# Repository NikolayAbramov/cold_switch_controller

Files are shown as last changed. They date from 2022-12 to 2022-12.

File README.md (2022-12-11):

# Cold switch controller
This is the specialized polarized relay controller intended to drive an RF switches, installed inside a cryostat. It's mainly
affordable for switches similar to famous Radial products: https://www.radiall.com/products/rf-microwave-switches.html. Such switches are commonly used in experiments with superconducting RF devices, and, particularly, with quantum circuits. 

The first problem with such switches at the liquid He temperature 4K and below is that the resistance of their coils drops by ~100 times compared to room temperature values and it's no longer possible to drive them with a nominal voltage. The second is that the heat dissipation during switching must be controlled to ensure normal cryostat operation. I't especially important in case of dilution refrigerators, commonly used for experiments with quantum devices. 

To overcome the above mentioned problems the controller uses an adjustable pulsed current source instead of a voltage source to drive the coils. Both the current and pulse duration can be adjusted to achieve a reliable switching and a minimal power dissipation. Due to it's flexibility, the controller can be used to control RF switches also at room temperature which makes it a useful tool to have in you lab for test and experiment automation.

It has a minimalistic formfactor of a 3U Eurorack module with absolutely no cotrols - everything is done using a web interface or an SCPI commands.

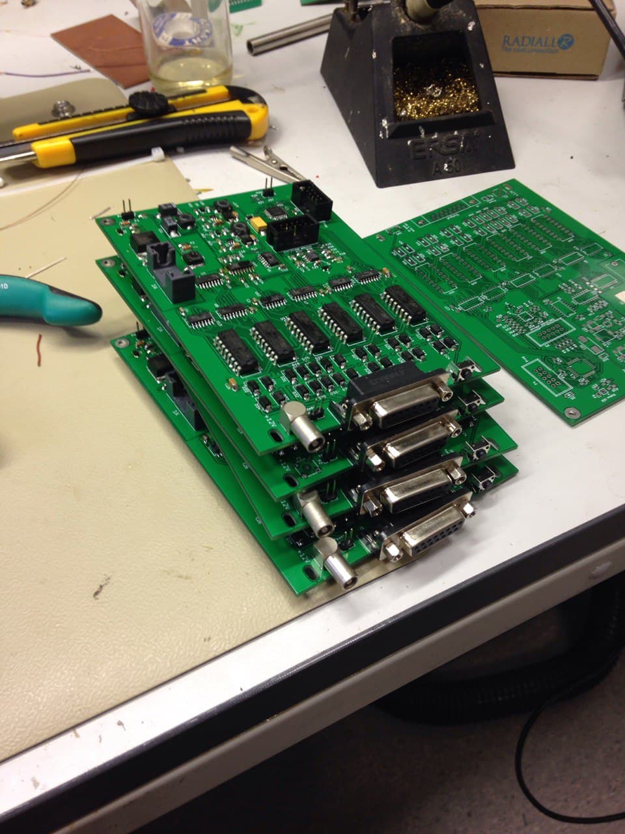
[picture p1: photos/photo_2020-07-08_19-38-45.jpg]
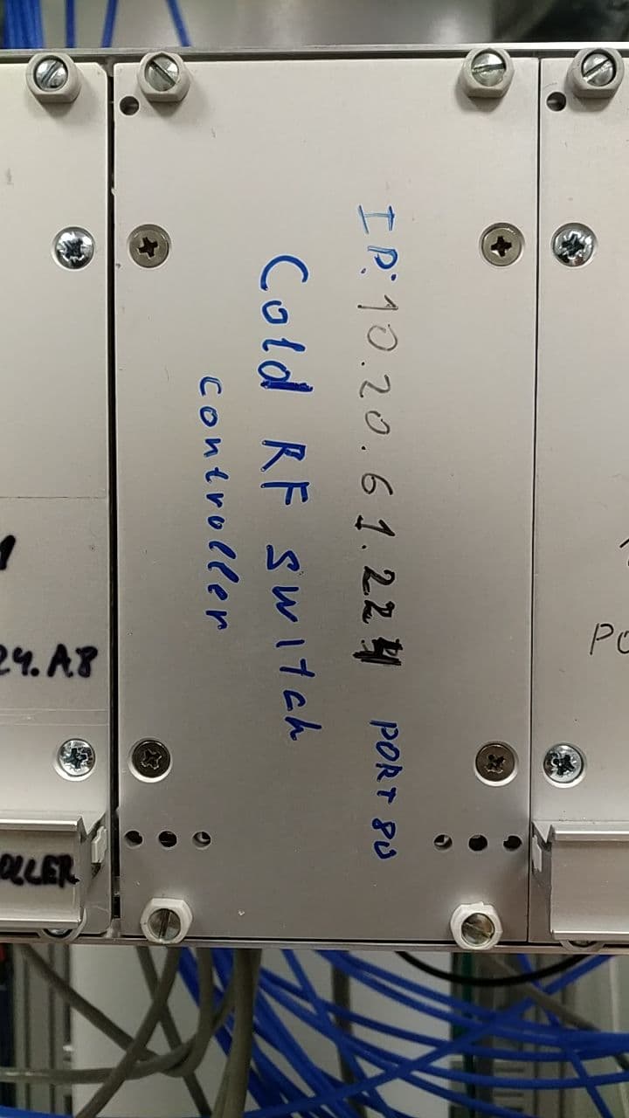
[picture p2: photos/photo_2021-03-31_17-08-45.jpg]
 

# Specs

 - Power: 12V, fully protected against overvoltage up to 30V and reversed polarity
 - Interface: Ethernet with web interface and SCPI commands
 - Output: 2 channels for polarized SPnT switches with number of positions n up to 6
 - Drive current: 10-600 mA
 - Drive pulse width: 1 - 700 ms
 - Switch coil voltage: 12 V for room temperature operation, any for cryogenic applications

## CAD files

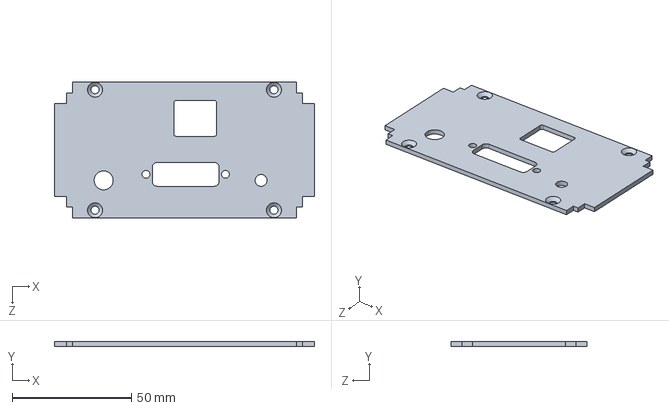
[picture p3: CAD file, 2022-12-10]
EuroBox_rear_panel/switch_controller_rear.SLDPRT
109.0 x 2.00 x 57.0 mm

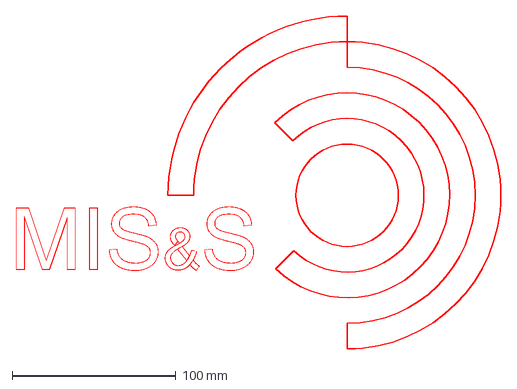
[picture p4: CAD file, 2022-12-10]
kicad/Logo_MISiS.dxf
295.7 x 203.1 mm

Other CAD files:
EuroBox_rear_panel/switch_controller_rear.SLDDRW

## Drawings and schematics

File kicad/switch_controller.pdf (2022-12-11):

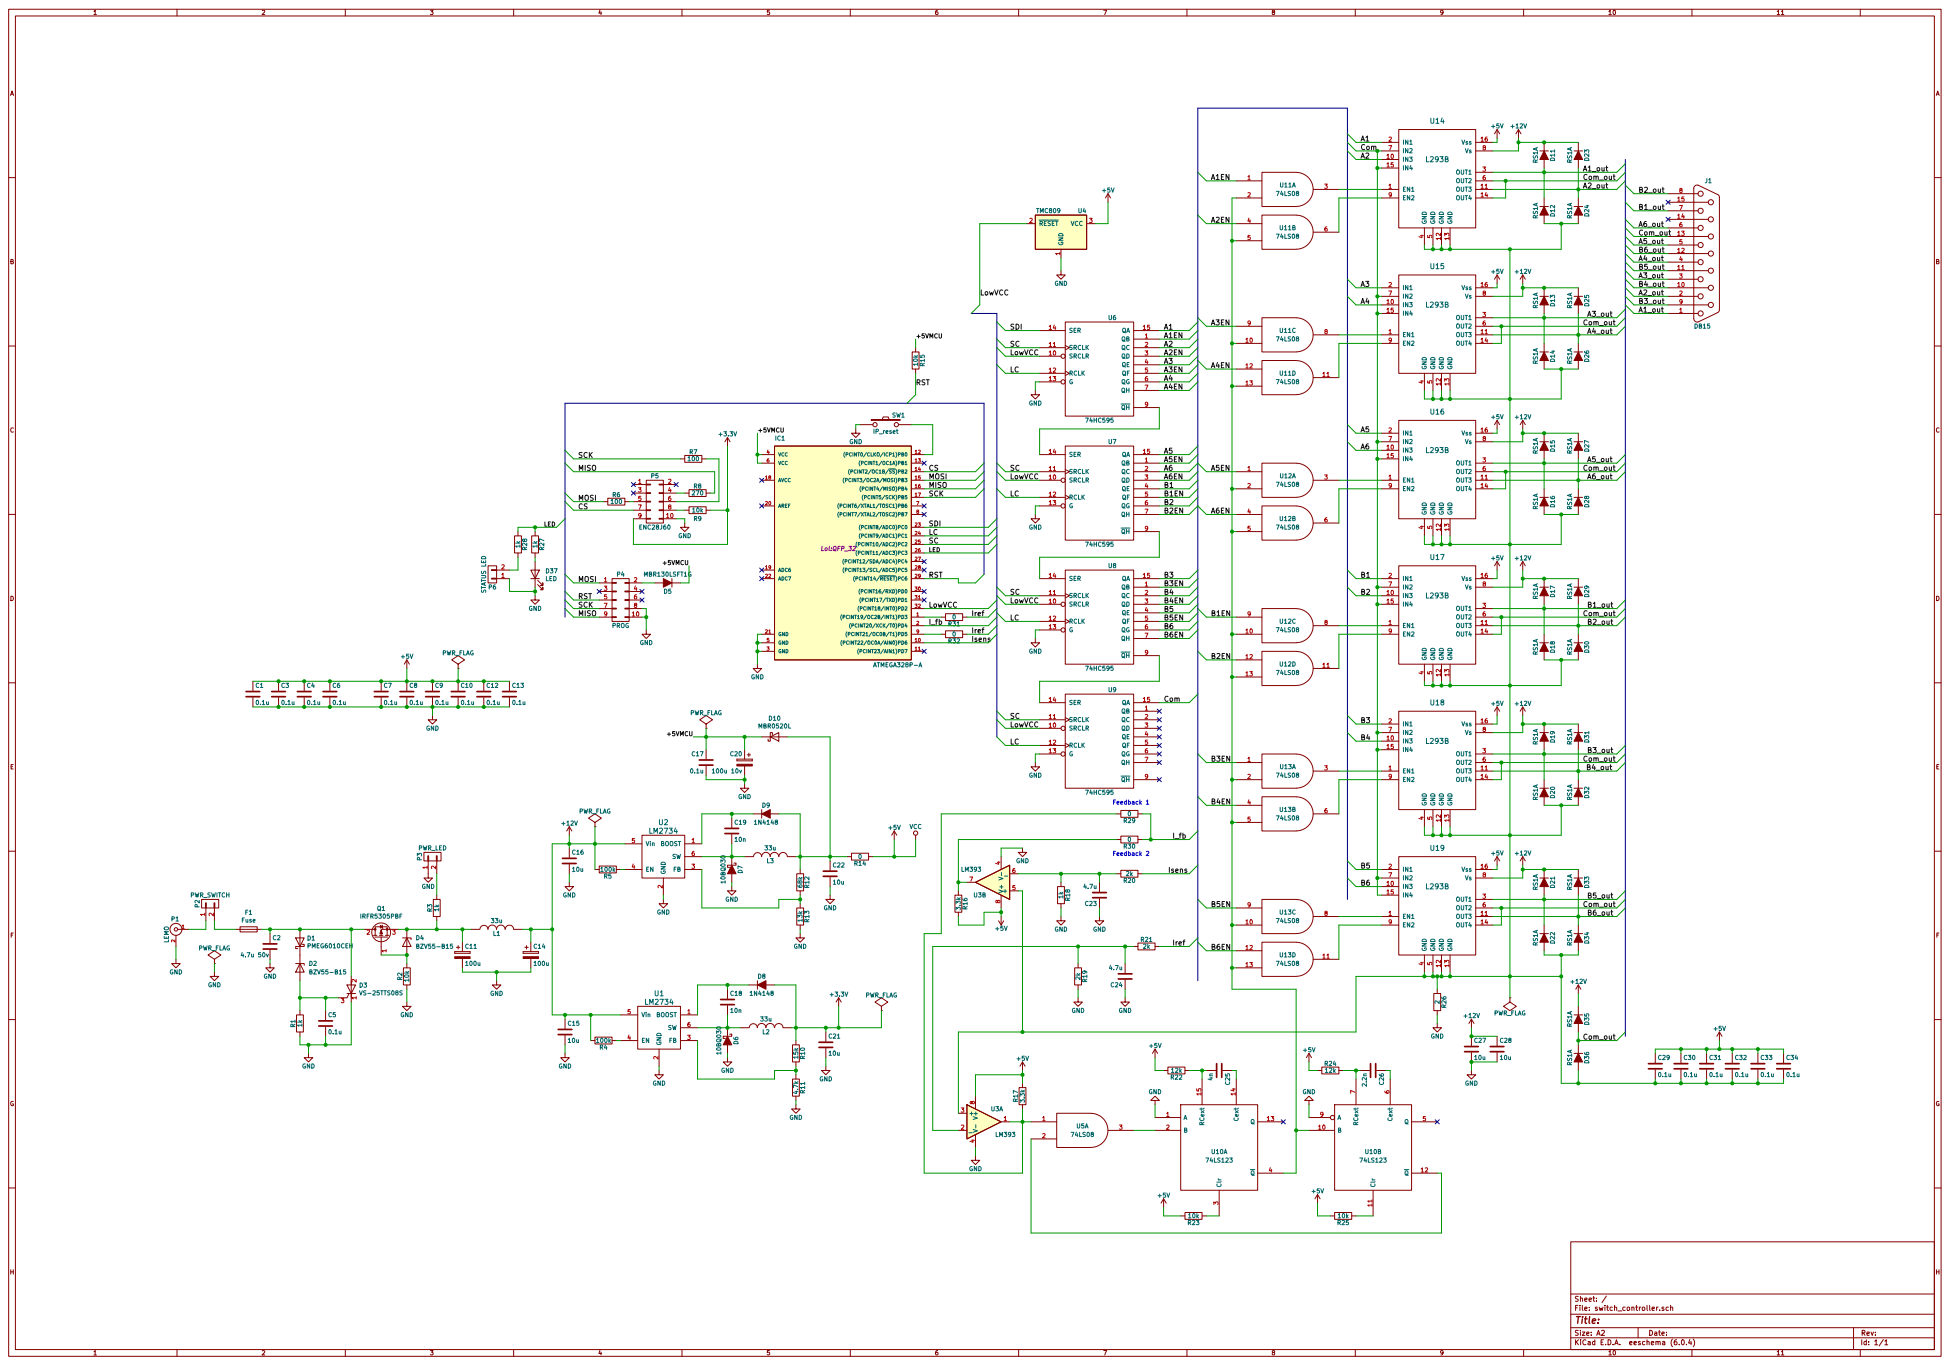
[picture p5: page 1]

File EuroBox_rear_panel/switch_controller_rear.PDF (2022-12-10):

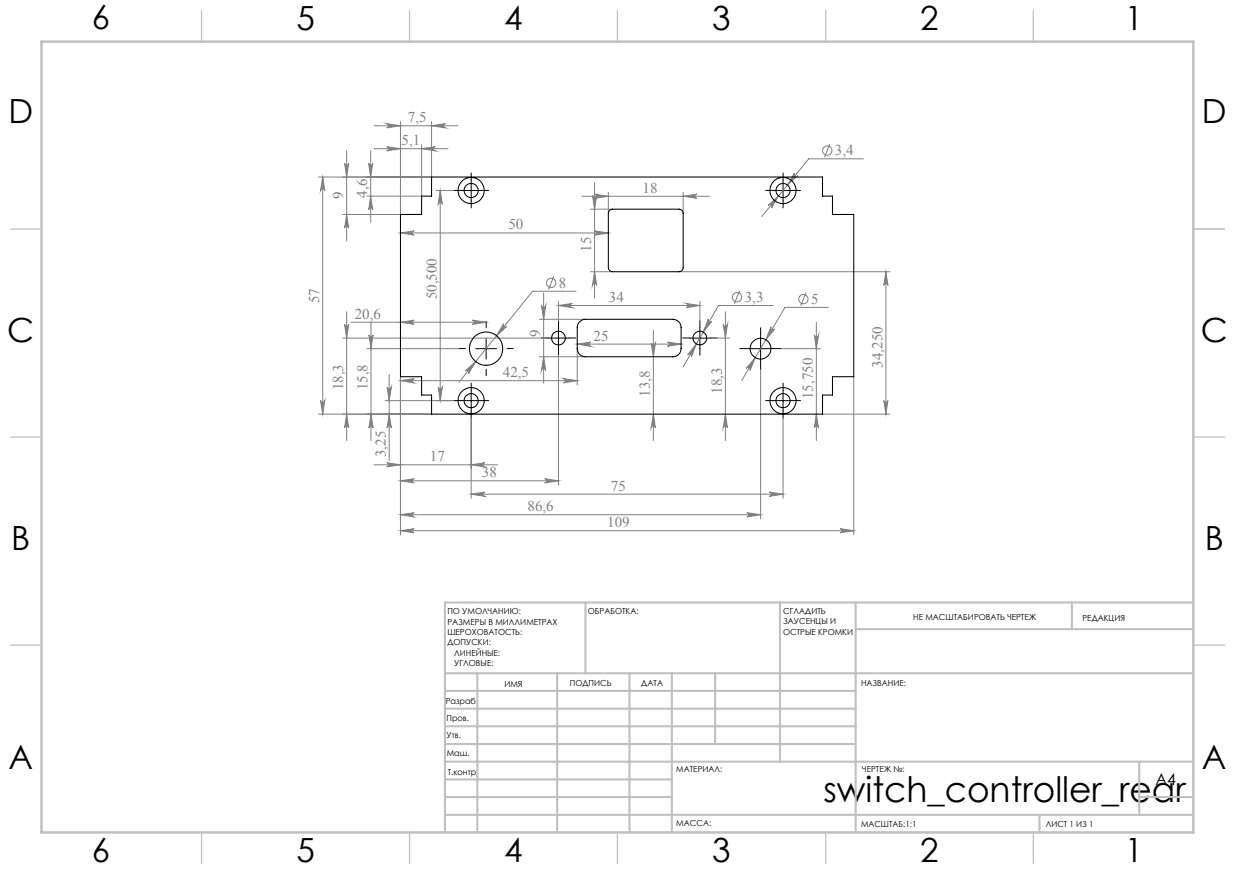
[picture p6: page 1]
МАСШТАБ:1:1; ЛИСТ 1 ИЗ 1; НЕ МАСШТАБИРОВАТЬ ЧЕРТЕЖ; РЕДАКЦИЯ; ЗАУСЕНЦЫ И ОСТРЫЕ КРОМКИ; ПО УМОЛЧАНИЮ:; ОБРАБОТКА:; РАЗМЕРЫ В МИЛЛИМЕТРАХ

ИМЯ | ПОДПИСЬ | ДАТА | | | | НАЗВАНИЕ:
Т.контр | | | | МАТЕРИАЛ: switch_controller_rear МАССА: | ЧЕРТЕЖ №: | A4

Разраб.
Пров.
Утв.
Маш.

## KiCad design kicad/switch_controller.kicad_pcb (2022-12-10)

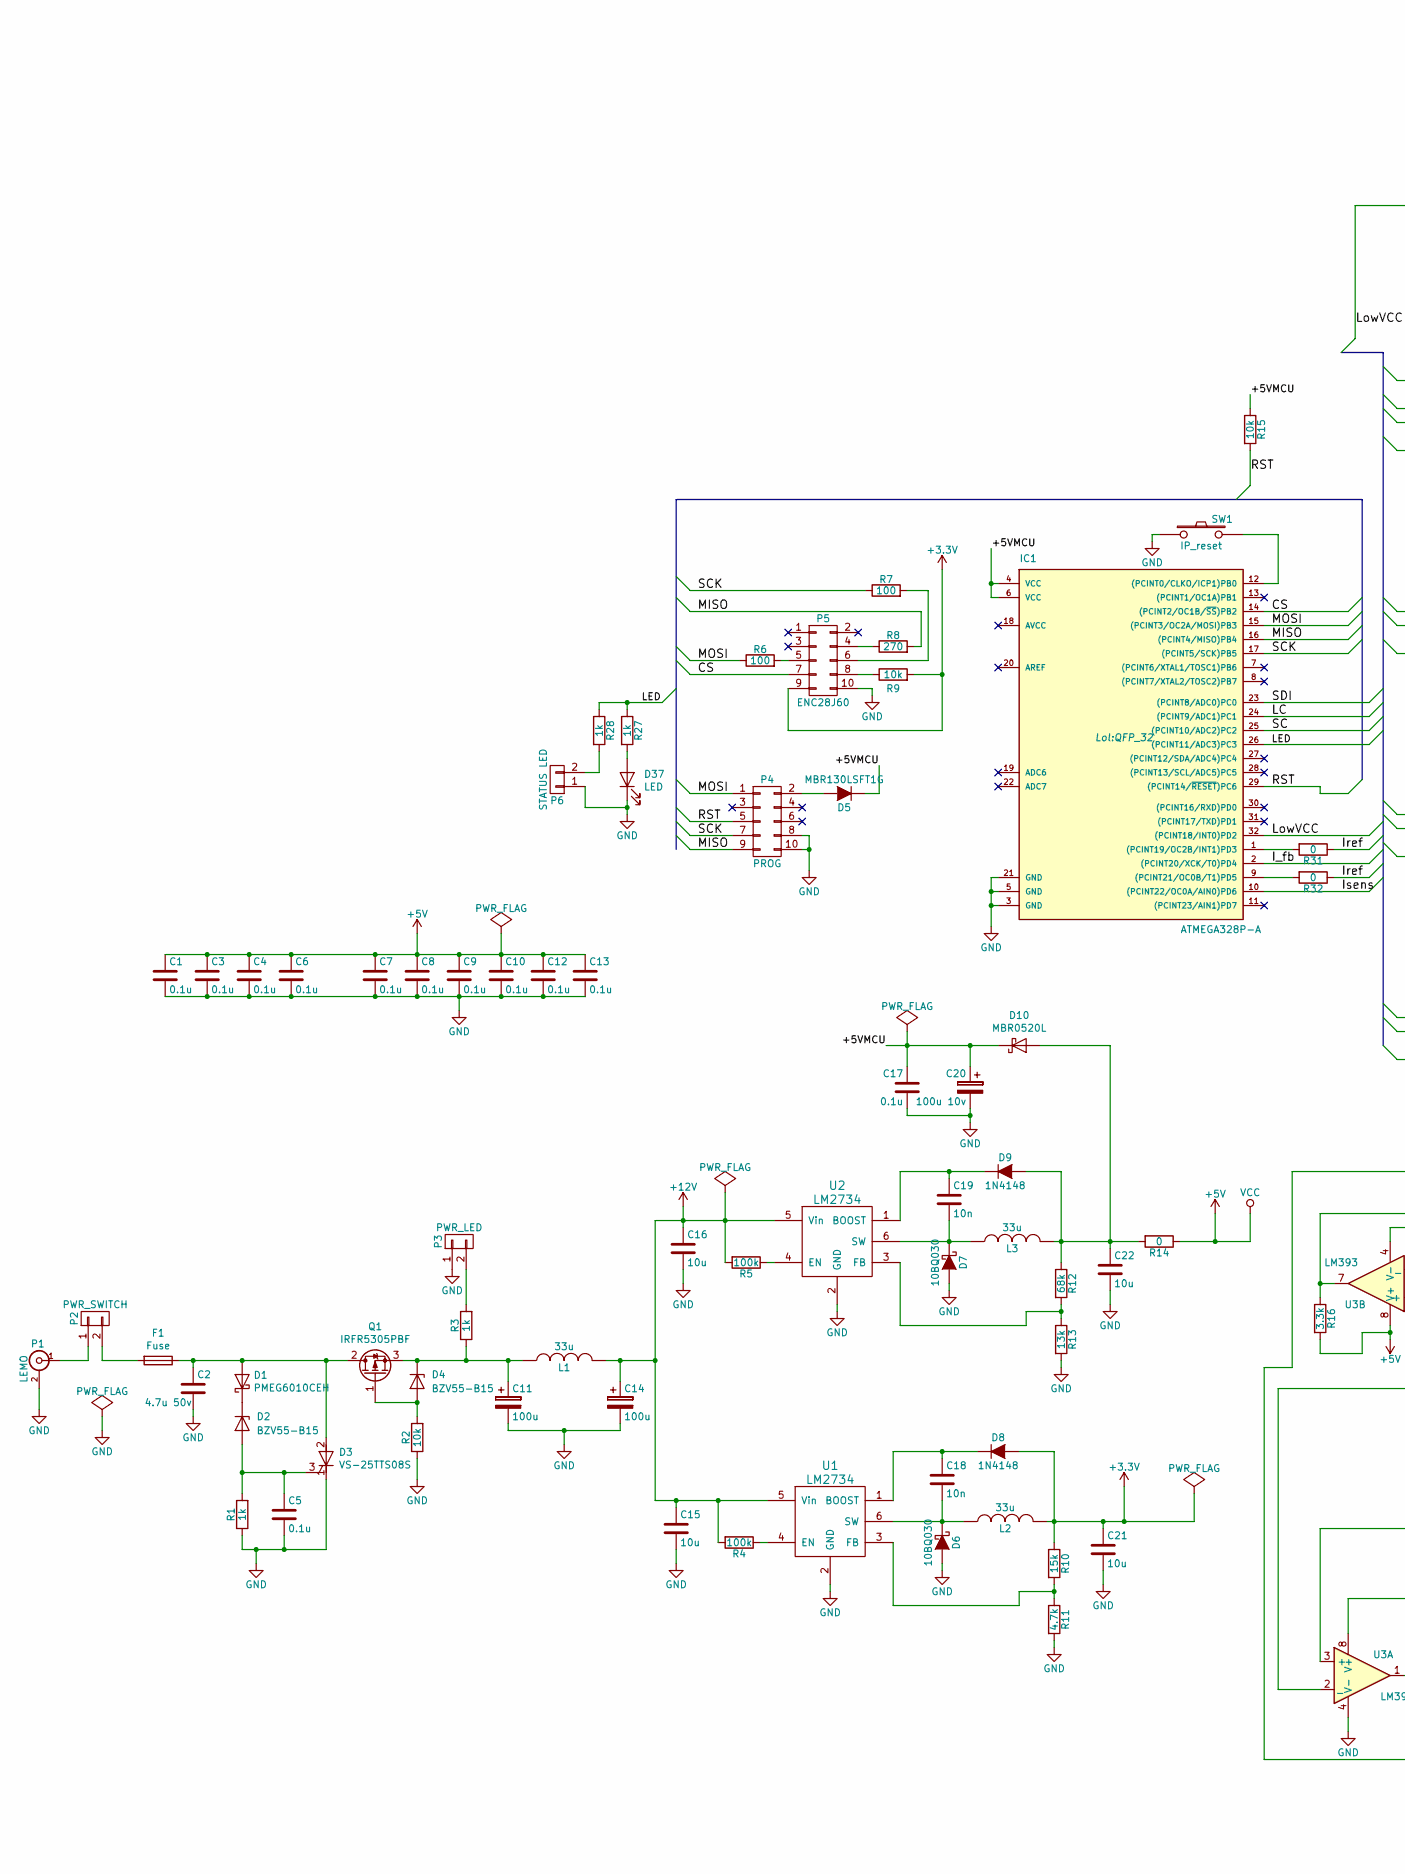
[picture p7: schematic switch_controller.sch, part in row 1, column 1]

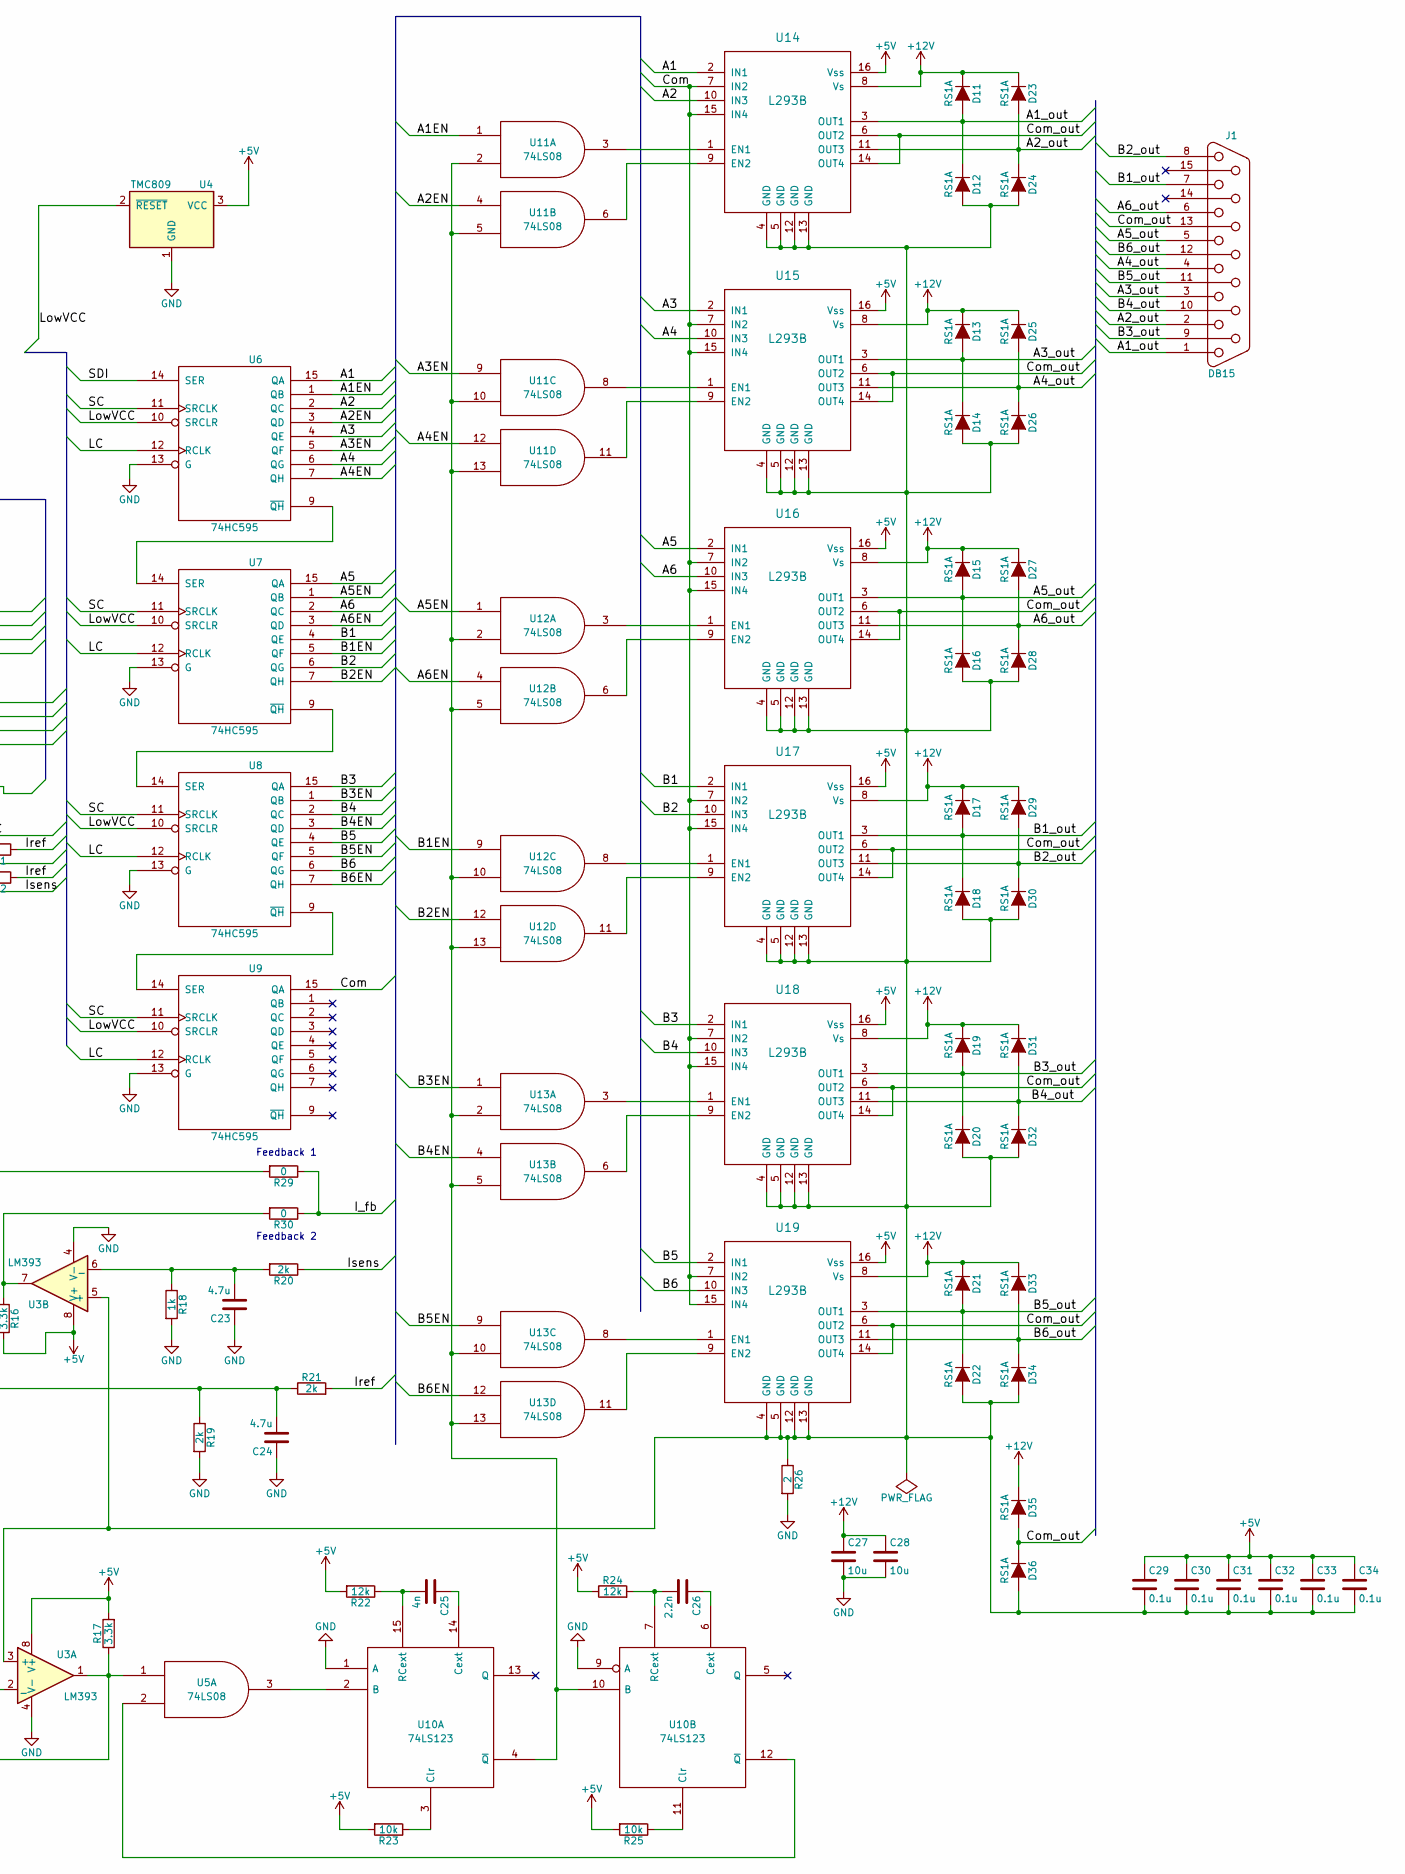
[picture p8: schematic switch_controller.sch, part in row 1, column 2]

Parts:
C1, C3, C4, C5, C6, C7, C8, C9, C10, C12, C13, C17, C29, C30, C31, C32, C33, C34: 0.1u; C_0805_HandSoldering
C2: 4.7u 50v; C_1206_HandSoldering
C11, C14: 100u; CP_Tantalum_Case-D_EIA-7343-31_Hand
C15, C16, C21, C22, C27, C28: 10u; C_1206_HandSoldering
C18, C19: 10n; C_0805_HandSoldering
C20: 100u 10v; CP_Tantalum_Case-D_EIA-7343-31_Hand
C23, C24: 4.7u; C_0805_HandSoldering
C25: 4n; C_0805_HandSoldering
C26: 2.2n; C_0805_HandSoldering
D1: PMEG6010CEH; D_SOD-123
D2, D4: BZV55-B15; D_1206
D3: VS-25TTS08S; TO-263-2
D5: MBR130LSFT1G; SOD-123
D6, D7: 10BQ030; DO-214AA
D8, D9: 1N4148; SOD-123
D10: MBR0520L; D_SOD-123
D11, D12, D13, D14, D15, D16, D17, D18, D19, D20, D21, D22, D23, D24, D25, D26, D27, D28, D29, D30, D31, D32, D33, D34, D35, D36: RS1A; DO-214BA
D37: LED; D_0603
F1: Fuse; FH-101
IC1: ATMEGA328P-A; QFP_32
J1: DB15; DB15FR
L1, L2, L3: 33u; SRR0603
P1: LEMO; LEMO_00_R
P2: PWR_SWITCH; Pin_Header_Straight_1x02_Pitch2.54mm
P3: PWR_LED; Pin_Header_Straight_1x02_Pitch2.54mm
P4: PROG; IDC_Header_Straight_10pins
P5: ENC28J60; IDC_Header_Straight_10pins
P6: STATUS LED; Pin_Header_Straight_1x02_Pitch2.54mm
Q1: IRFR5305PBF; TO-252-2
R1, R3, R18, R27, R28: 1k; R_0805_HandSoldering
R2, R9, R15, R23, R25: 10k; R_0805_HandSoldering
R4, R5: 100k; R_0805_HandSoldering
R6, R7: 100; R_0805_HandSoldering
R8: 270; R_0805_HandSoldering
R10: 15k; R_0805_HandSoldering
R11: 4.7k; R_0805_HandSoldering
R12: 68k; R_0805_HandSoldering
R13: 13k; R_0805_HandSoldering
R14, R29, R30, R31, R32: 0; R_0805_HandSoldering
R16, R17: 3.3k; R_0805_HandSoldering
R19, R20, R21: 2k; R_0805_HandSoldering
R22, R24: 12k; R_0805_HandSoldering
R26: 2; R_1206_HandSoldering
SW1: IP_reset; SW_Tactile_SPST_Angled
U1, U2: LM2734; TSOT-23-6
U3: LM393; SOIC-8-N
U4: TMC809; SOT-23
U5, U11, U12, U13: 74LS08; SOIC-14_N
U6, U7, U8, U9: 74HC595; SO-16-N
U10: 74LS123; SO-16-N
U14, U15, U16, U17, U18, U19: L293B; DIP-16_W7.62mm_LongPads

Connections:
+3V3: C21.1, D8.2 (A), L2.2, P5.9, R9.2, R10.1
+5V: C1.1, C3.1, C4.1, C6.1, C7.1, C8.1, C9.1, C10.1, C12.1, C13.1, C29.1, C30.1, C31.1, C32.1, C33.1, C34.1, R14.1, R16.2, R17.2, R22.2, R23.2, R24.1, R25.2, U3.8 (V+), U4.3 (VCC), U5.14 (VCC), U6.16 (VCC), U7.16 (VCC), U8.16 (VCC), U9.16 (VCC), U10.16 (VCC), U11.14 (VCC), U12.14 (VCC), U13.14 (VCC), U14.16 (Vss), U15.16 (Vss), U16.16 (Vss), U17.16 (Vss), U18.16 (Vss), U19.16 (Vss)
+12V: C14.1, C15.1, C16.1, C27.1, C28.1, D11.1 (K), D13.1 (K), D15.1 (K), D17.1 (K), D19.1 (K), D21.1 (K), D23.1 (K), D25.1 (K), D27.1 (K), D29.1 (K), D31.1 (K), D33.1 (K), D35.1 (K), L1.2, R4.2, R5.2, U1.5 (Vin), U2.5 (Vin), U14.8 (Vs), U15.8 (Vs), U16.8 (Vs), U17.8 (Vs), U18.8 (Vs), U19.8 (Vs)
/+5VMCU: C17.1, C20.1, D5.1 (K), D10.1 (K), IC1.4 (VCC), IC1.6 (VCC), R15.1
/A1: U6.15 (QA), U14.2 (IN1)
/A1EN: U6.1 (QB), U11.1
/A1_out: D11.2 (A), D12.1 (K), J1.1, U14.3 (OUT1)
/A2: U6.2 (QC), U14.10 (IN3)
/A2EN: U6.3 (QD), U11.4
/A2_out: D23.2 (A), D24.1 (K), J1.2, U14.11 (OUT3)
/A3: U6.4 (QE), U15.2 (IN1)
/A3EN: U6.5 (QF), U11.9
/A3_out: D13.2 (A), D14.1 (K), J1.3, U15.3 (OUT1)
/A4: U6.6 (QG), U15.10 (IN3)
/A4EN: U6.7 (QH), U11.12
/A4_out: D25.2 (A), D26.1 (K), J1.4, U15.11 (OUT3)
/A5: U7.15 (QA), U16.2 (IN1)
/A5EN: U7.1 (QB), U12.1
/A5_out: D15.2 (A), D16.1 (K), J1.5, U16.3 (OUT1)
/A6: U7.2 (QC), U16.10 (IN3)
/A6EN: U7.3 (QD), U12.4
/A6_out: D27.2 (A), D28.1 (K), J1.6, U16.11 (OUT3)
/B1: U7.4 (QE), U17.2 (IN1)
/B1EN: U7.5 (QF), U12.9
/B1_out: D17.2 (A), D18.1 (K), J1.7, U17.3 (OUT1)
/B2: U7.6 (QG), U17.10 (IN3)
/B2EN: U7.7 (QH), U12.12
/B2_out: D29.2 (A), D30.1 (K), J1.8, U17.11 (OUT3)
/B3: U8.15 (QA), U18.2 (IN1)
/B3EN: U8.1 (QB), U13.1
/B3_out: D19.2 (A), D20.1 (K), J1.9, U18.3 (OUT1)
/B4: U8.2 (QC), U18.10 (IN3)
/B4EN: U8.3 (QD), U13.4
/B4_out: D31.2 (A), D32.1 (K), J1.10, U18.11 (OUT3)
/B5: U8.4 (QE), U19.2 (IN1)
/B5EN: U8.5 (QF), U13.9
/B5_out: D21.2 (A), D22.1 (K), J1.11 (P111), U19.3 (OUT1)
/B6: U8.6 (QG), U19.10 (IN3)
/B6EN: U8.7 (QH), U13.12
/B6_out: D33.2 (A), D34.1 (K), J1.12, U19.11 (OUT3)
/CS: IC1.14 ((PCINT2/OC1B/~SS~)PB2), P5.7
/Com: U9.15 (QA), U14.7 (IN2), U14.15 (IN4), U15.7 (IN2), U15.15 (IN4), U16.7 (IN2), U16.15 (IN4), U17.7 (IN2), U17.15 (IN4), U18.7 (IN2), U18.15 (IN4), U19.7 (IN2), U19.15 (IN4)
/Com_out: D35.2 (A), D36.1 (K), J1.13, U14.6 (OUT2), U14.14 (OUT4), U15.6 (OUT2), U15.14 (OUT4), U16.6 (OUT2), U16.14 (OUT4), U17.6 (OUT2), U17.14 (OUT4), U18.6 (OUT2), U18.14 (OUT4), U19.6 (OUT2), U19.14 (OUT4)
/I_fb: IC1.2 ((PCINT20/XCK/T0)PD4), R29.1, R30.1
/Iref: R21.2, R31.1, R32.1
/Isens: IC1.10 ((PCINT22/OC0A/AIN0)PD6), R20.1
/LC: IC1.24 ((PCINT9/ADC1)PC1), U6.12 (RCLK), U7.12 (RCLK), U8.12 (RCLK), U9.12 (RCLK)
/LED: IC1.26 ((PCINT11/ADC3)PC3), R27.1, R28.1
/LowVCC: IC1.32 ((PCINT18/INT0)PD2), U4.2 (~RESET~), U6.10 (SRCLR), U7.10 (SRCLR), U8.10 (SRCLR), U9.10 (SRCLR)
/MISO: IC1.16 ((PCINT4/MISO)PB4), P4.9, R8.2
/MOSI: IC1.15 ((PCINT3/OC2A/MOSI)PB3), P4.1, R6.1
/RST: IC1.29 ((PCINT14/~RESET~)PC6), P4.5, R15.2
/SC: IC1.25 ((PCINT10/ADC2)PC2), U6.11 (SRCLK), U7.11 (SRCLK), U8.11 (SRCLK), U9.11 (SRCLK)
/SCK: IC1.17 ((PCINT5/SCK)PB5), P4.7, R7.1
/SDI: IC1.23 ((PCINT8/ADC0)PC0), U6.14 (SER)
GND: C1.2, C2.2, C3.2, C4.2, C5.2, C6.2, C7.2, C8.2, C9.2, C10.2, C11.2, C12.2, C13.2, C14.2, C15.2, C16.2, C17.2, C20.2, C21.2, C22.2, C23.1, C24.1, C27.2, C28.2, D3.1 (K), D6.2 (A), D7.2 (A), D37.1 (K), IC1.3 (GND), IC1.5 (GND), IC1.21 (GND), P1.2 (Ext), P3.1, P4.8, P4.10, P5.10, P6.1, R1.1, R2.1, R11.2, R13.2, R18.2, R19.2, R26.2, SW1.1, U1.2 (GND), U2.2 (GND), U3.4 (V-), U4.1 (GND), U5.7 (GND), U6.8 (GND), U6.13 (G), U7.8 (GND), U7.13 (G), U8.8 (GND), U8.13 (G), U9.8 (GND), U9.13 (G), U10.1 (A), U10.8 (GND), U10.9 (A), U11.7 (GND), U12.7 (GND), U13.7 (GND)
unnamed: C2.1, D1.2 (A), D3.2 (A), F1.1, Q1.2 (D)
unnamed: C5.1, D2.2 (A), D3.3 (G), R1.2
unnamed: C11.1, D4.1 (K), L1.1, Q1.3 (S), R3.1
unnamed: C18.1, D8.1 (K), U1.1 (BOOST)
unnamed: C18.2, D6.1 (K), L2.1, U1.6 (SW)
unnamed: C19.1, D9.1 (K), U2.1 (BOOST)
unnamed: C19.2, D7.1 (K), L3.1, U2.6 (SW)
unnamed: C22.1, D9.2 (A), D10.2 (A), L3.2, R12.1, R14.2
unnamed: C23.2, R18.1, R20.2, U3.6 (_)
unnamed: C24.2, R19.1, R21.1, U3.2 (_)
unnamed: C25.1, U10.14 (Cext)
unnamed: C25.2, R22.1, U10.15 (RCext)
unnamed: C26.1, U10.6 (Cext)
unnamed: C26.2, R24.2, U10.7 (RCext)
unnamed: C29.2, C30.2, C31.2, C32.2, C33.2, C34.2, D12.2 (A), D14.2 (A), D16.2 (A), D18.2 (A), D20.2 (A), D22.2 (A), D24.2 (A), D26.2 (A), D28.2 (A), D30.2 (A), D32.2 (A), D34.2 (A), D36.2 (A), R26.1, U3.3 (+), U3.5 (+), U14.4 (GND), U14.5 (GND), U14.12 (GND), U14.13 (GND), U15.4 (GND), U15.5 (GND), U15.12 (GND), U15.13 (GND), U16.4 (GND), U16.5 (GND), U16.12 (GND), U16.13 (GND), U17.4 (GND), U17.5 (GND), U17.12 (GND), U17.13 (GND), U18.4 (GND), U18.5 (GND), U18.12 (GND), U18.13 (GND), U19.4 (GND), U19.5 (GND), U19.12 (GND), U19.13 (GND)
unnamed: D1.1 (K), D2.1 (K)
unnamed: D4.2 (A), Q1.1 (G), R2.2
unnamed: D5.2 (A), P4.2
unnamed: D37.2 (A), R27.2
unnamed: F1.2, P2.2
unnamed: IC1.1 ((PCINT19/OC2B/INT1)PD3), R31.2
unnamed: IC1.9 ((PCINT21/OC0B/T1)PD5), R32.2
unnamed: IC1.12 ((PCINT0/CLKO/ICP1)PB0), SW1.2
unnamed: P1.1 (In), P2.1
unnamed: P3.2, R3.2
unnamed: P5.4, R8.1
unnamed: P5.5, R6.2
unnamed: P5.6, R7.2
unnamed: P5.8, R9.1
unnamed: P6.2, R28.2
unnamed: R4.1, U1.4 (EN)
unnamed: R5.1, U2.4 (EN)
unnamed: R10.2, R11.1, U1.3 (FB)
unnamed: R12.2, R13.1, U2.3 (FB)
unnamed: R16.1, R30.2, U3.7
unnamed: R17.1, R29.2, U3.1, U5.1
unnamed: R23.1, U10.3 (Clr)
unnamed: R25.1, U10.11 (Clr)
unnamed: U6.9 (~QH), U7.14 (SER)
unnamed: U7.9 (~QH), U8.14 (SER)
unnamed: U8.9 (~QH), U9.14 (SER)
unnamed: U5.3, U10.2 (B)
unnamed: U10.4 (~Q), U10.10 (B), U11.2, U11.5, U11.10, U11.13, U12.2, U12.5, U12.10, U12.13, U13.2, U13.5, U13.10, U13.13
unnamed: U5.2, U10.12 (~Q)
unnamed: U11.3, U14.1 (EN1)
unnamed: U11.6, U14.9 (EN2)
unnamed: U11.8, U15.1 (EN1)
unnamed: U11.11, U15.9 (EN2)
unnamed: U12.3, U16.1 (EN1)
unnamed: U12.6, U16.9 (EN2)
unnamed: U12.8, U17.1 (EN1)
unnamed: U12.11, U17.9 (EN2)
unnamed: U13.3, U18.1 (EN1)
unnamed: U13.6, U18.9 (EN2)
unnamed: U13.8, U19.1 (EN1)
unnamed: U13.11, U19.9 (EN2)

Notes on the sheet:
Feedback 1
Feedback 2

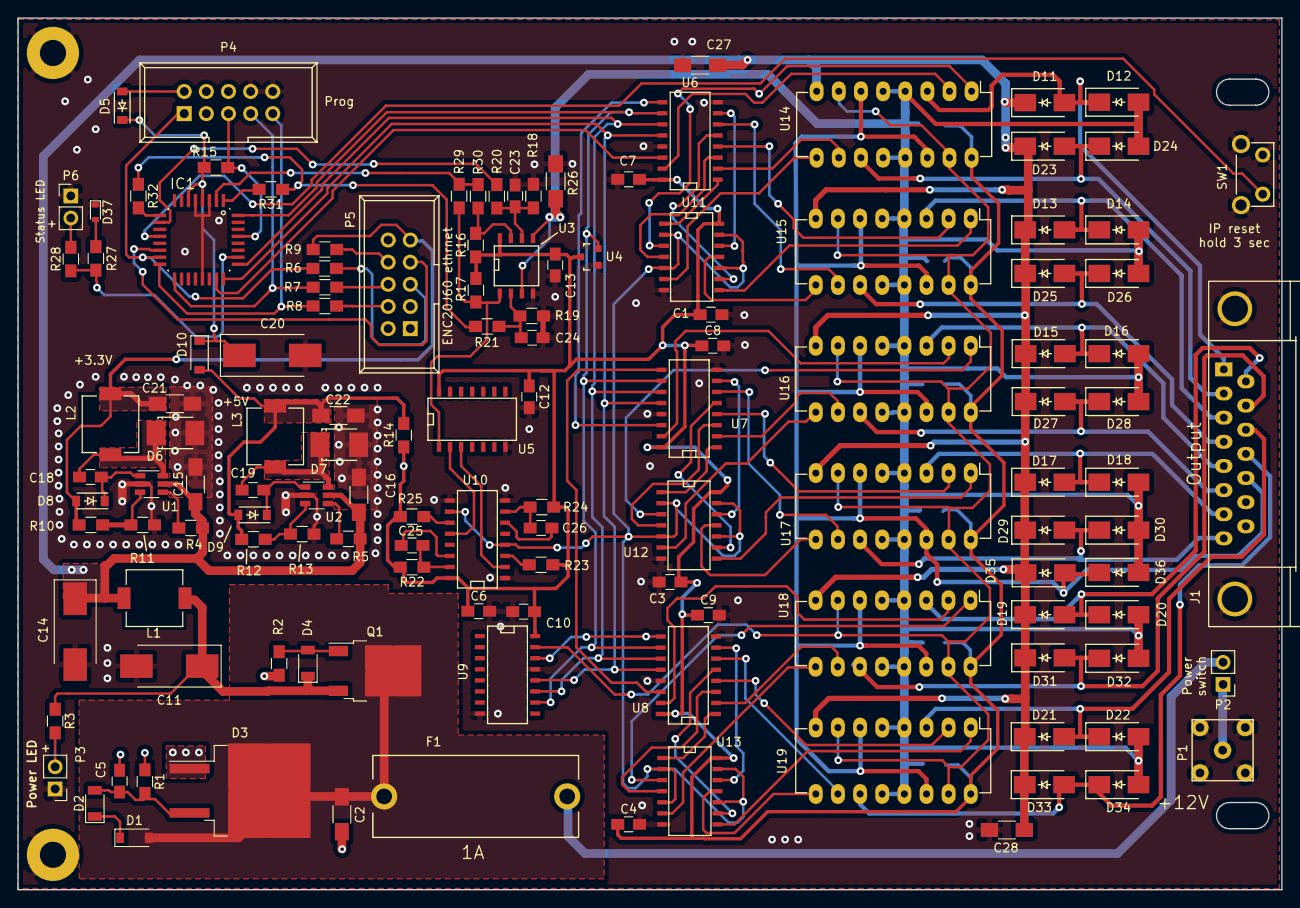
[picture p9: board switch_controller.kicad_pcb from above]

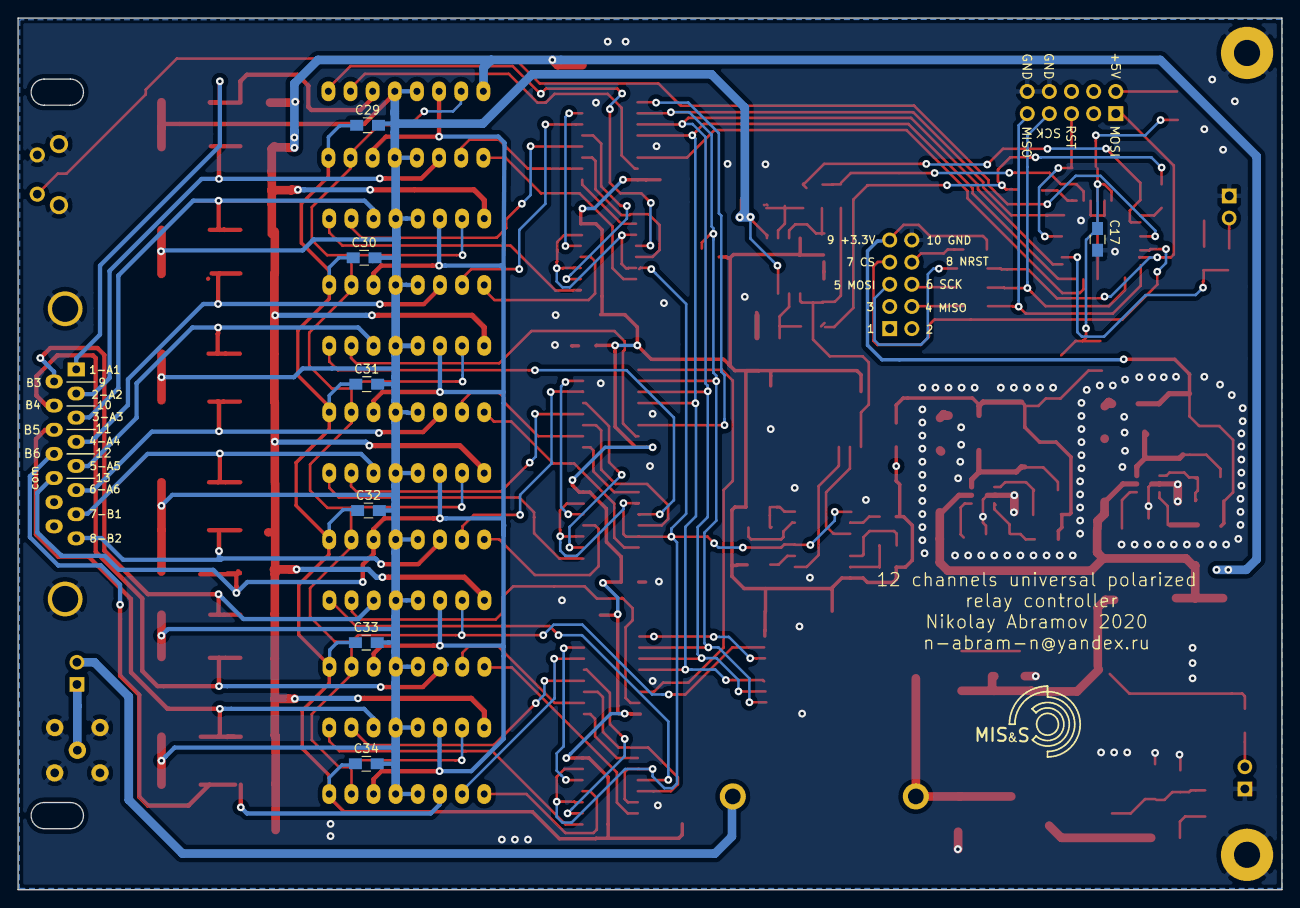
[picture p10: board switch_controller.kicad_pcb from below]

Board: 2 copper layers, 145.0 x 100.0 mm, 136 parts (7 on the bottom side), 112 nets.

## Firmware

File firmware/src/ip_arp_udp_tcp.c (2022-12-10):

/*********************************************
 * vim:sw=8:ts=8:si:et
 * To use the above modeline in vim you must have "set modeline" in your .vimrc
 *
 * Author: Guido Socher 
 * Copyright:LGPL V2
 * See http://www.gnu.org/licenses/old-licenses/lgpl-2.0.html
 *
 * IP, Arp, UDP and TCP functions.
 *
 * The TCP implementation uses some size optimisations which are valid
 * only if all data can be sent in one single packet. This is however
 * not a big limitation for a microcontroller as you will anyhow use
 * small web-pages. The web server must send the entire web page in one
 * packet. The client "web browser" as implemented here can also receive
 * large pages.
 *
 * Chip type           : ATMEGA88/168/328/644 with ENC28J60
 *********************************************/
#include <avr/io.h>
#include <avr/pgmspace.h>
#include <string.h>
#include <ctype.h>
#include <stdlib.h>
#include "net.h"
#include "enc28j60.h"
#include "ip_config.h"

// I use them to debug stuff:
#define LEDOFF PORTB|=(1<<PORTB1)
#define LEDON PORTB&=~(1<<PORTB1)
#define LEDISOFF PORTB&(1<<PORTB1)
//
static uint8_t macaddr[6];
static uint8_t ipaddr[4]={0,0,0,0};
static uint8_t seqnum=0xa; // my initial tcp sequence number
static void (*icmp_callback)(uint8_t *ip);
//
#if defined (NTP_client) || defined (UDP_client) || defined (TCP_client) || defined (PING_client)
#define ARP_MAC_resolver_client 1
#define ALL_clients 1
#endif
#if defined (WWW_client) || defined (TCP_client) 
// just lower byte, the upper byte is TCPCLIENT_SRC_PORT_H:
static uint8_t tcpclient_src_port_l=1; 
static uint8_t tcp_fd=0; // a file descriptor, will be encoded into the port
static uint8_t tcp_otherside_ip[4];
static uint8_t tcp_dst_mac[6]; // normally the gateway via which we want to send
static uint8_t tcp_client_state=0;
static uint16_t tcp_client_port=0;
// This function will be called if we ever get a result back from the
// TCP connection to the sever:
// close_connection= your_client_tcp_result_callback(uint8_t fd, uint8_t statuscode,uint16_t data_start_pos_in_buf, uint16_t len_of_data){...your code}
// statuscode=0 means the buffer has valid data
static uint8_t (*client_tcp_result_callback)(uint8_t,uint8_t,uint16_t,uint16_t);
// len_of_data_filled_in=your_client_tcp_datafill_callback(uint8_t fd){...your code}
static uint16_t (*client_tcp_datafill_callback)(uint8_t);
#endif

#define TCPCLIENT_SRC_PORT_H 11

#if defined (WWW_client)
// WWW_client uses TCP_client
#define TCP_client 1
static uint8_t www_fd=0;
static uint8_t browsertype=0; // 0 = get, 1 = post
static void (*client_browser_callback)(uint16_t,uint16_t,uint16_t); // the fields are: uint16_t webstatuscode,uint16_t datapos,uint16_t len; datapos is start of http data and len the the length of that data
static const char *client_additionalheaderline_p; // null pointer or pointer to a string in progmem
static char *client_postval;
static const char *client_urlbuf_p; // null pointer or pointer to a string in progmem
static char *client_urlbuf_var;
static const char *client_hoststr;
static uint8_t *bufptr=0; // ugly workaround for backward compatibility
#endif


#ifdef ARP_MAC_resolver_client
// This function will be called if we ever get a result back from the
// the arp request we sent out.
void (*client_arp_result_callback)(uint8_t*,uint8_t,uint8_t*);
static int16_t arp_delaycnt=1;
static uint8_t arpip[4];  // IP to find via arp
static uint8_t arpip_state=0; // 0 at poweron, 1=req sent no answer yet, 2=have mac, 8=ready to accept an arp reply
static uint8_t arp_reference_number=0;
#define WGW_INITIAL_ARP 1
#define WGW_HAVE_MAC 2
#define WGW_ACCEPT_ARP_REPLY 8
#endif

#ifdef WWW_server
static uint8_t wwwport_l=80; // server port
static uint8_t wwwport_h=0;  // Note: never use same as TCPCLIENT_SRC_PORT_H
static uint16_t info_data_len=0;
#endif

#if defined (ALL_clients)
static uint8_t ipnetmask[4]={255,255,255,255};
#endif
#if defined (ALL_clients) || defined (WOL_client)
static uint8_t ipid=0x2; // IP-identification, it works as well if you do not change it but it is better to fill the field, we count this number up and wrap.
const char iphdr[] PROGMEM ={0x45,0,0,0x82,0,0,0x40,0,0x20}; // 0x82 is the total len on ip, 0x20 is ttl (time to live), the second 0,0 is IP-identification and may be changed.
#endif

#define CLIENTMSS 750
#define TCP_DATA_START ((uint16_t)TCP_SRC_PORT_H_P+(buf[TCP_HEADER_LEN_P]>>4)*4)
const char arpreqhdr[] PROGMEM ={0,1,8,0,6,4,0,1};
#ifdef NTP_client
const char ntpreqhdr[] PROGMEM ={0xe3,0,4,0xfa,0,1,0,0,0,1};
#endif

// The Ip checksum is calculated over the ip header only starting
// with the header length field and a total length of 20 bytes
// unitl ip.dst
// You must set the IP checksum field to zero before you start
// the calculation.
// len for ip is 20.
//
// For UDP/TCP we do not make up the required pseudo header. Instead we 
// use the ip.src and ip.dst fields of the real packet:
// The udp checksum calculation starts with the ip.src field
// Ip.src=4bytes,Ip.dst=4 bytes,Udp header=8bytes + data length=16+len
// In other words the len here is 8 + length over which you actually
// want to calculate the checksum.
// You must set the checksum field to zero before you start
// the calculation.
// The same algorithm is also used for udp and tcp checksums.
// len for udp is: 8 + 8 + data length
// len for tcp is: 4+4 + 20 + option len + data length
//
// For more information on how this algorithm works see:
// http://www.netfor2.com/checksum.html
// http://www.msc.uky.edu/ken/cs471/notes/chap3.htm
// The RFC has also a C code example: http://www.faqs.org/rfcs/rfc1071.html
uint16_t checksum(uint8_t *buf, uint16_t len,uint8_t type){
        // type 0=ip , icmp
        //      1=udp
        //      2=tcp
        uint32_t sum = 0;

        //if(type==0){    
        //        // do not add anything, standard IP checksum as described above
        //        // Usable for ICMP and IP header
        //}
        if(type==1){
                sum+=IP_PROTO_UDP_V; // protocol udp
                // the length here is the length of udp (data+header len)
                // =length given to this function - (IP.scr+IP.dst length)
                sum+=len-8; // = real udp len
        }
        if(type==2){
                sum+=IP_PROTO_TCP_V; 
                // the length here is the length of tcp (data+header len)
                // =length given to this function - (IP.scr+IP.dst length)
                sum+=len-8; // = real tcp len
        }
        // build the sum of 16bit words
        while(len >1){
                sum += 0xFFFF & (((uint32_t)*buf<<8)|*(buf+1));
                buf+=2;
                len-=2;
        }
        // if there is a byte left then add it (padded with zero)
        if (len){
                sum += ((uint32_t)(0xFF & *buf))<<8;
        }
        // now calculate the sum over the bytes in the sum
        // until the result is only 16bit long
        while (sum>>16){
                sum = (sum & 0xFFFF)+(sum >> 16);
        }
        // build 1's complement:
        return( (uint16_t) sum ^ 0xFFFF);
}

void init_mac(uint8_t *mymac){
        if (mymac){
                memcpy(macaddr,mymac,6);
        }
}

#if defined (ALL_clients)
void client_ifconfig(uint8_t *ip,uint8_t *netmask)
{
        uint8_t i;
        if (ip){
                i=0;while(i<4){ipaddr[i]=ip[i];i++;}
        }
        if (netmask){
                i=0;while(i<4){ipnetmask[i]=netmask[i];i++;}
        }
}

// returns 1 if destip must be routed via the GW. Returns 0 if destip is on the local LAN
uint8_t route_via_gw(uint8_t *destip)
{
	uint8_t i=0;
	while(i<4){
		if ((destip[i] & ipnetmask[i]) != (ipaddr[i] & ipnetmask[i])){
			return(1);
		}
		i++;
	}
	return(0);
}
#endif


uint8_t check_ip_message_is_from(uint8_t *buf,uint8_t *ip)
{
        uint8_t i=0;
        while(i<4){
                if(buf[IP_SRC_P+i]!=ip[i]){
                        return(0);
                }
                i++;
        }
        return(1);
}

uint8_t eth_type_is_arp_and_my_ip(uint8_t *buf,uint16_t len){
        uint8_t i=0;
        //  
        if (len<41){
                return(0);
        }
        if(buf[ETH_TYPE_H_P] != ETHTYPE_ARP_H_V || 
           buf[ETH_TYPE_L_P] != ETHTYPE_ARP_L_V){
                return(0);
        }
        while(i<4){
                if(buf[ETH_ARP_DST_IP_P+i] != ipaddr[i]){
                        return(0);
                }
                i++;
        }
        return(1);
}

uint8_t eth_type_is_ip_and_my_ip(uint8_t *buf,uint16_t len){
        uint8_t i=0;
        //eth+ip+udp header is 42
        if (len<42){
                return(0);
        }
        if(buf[ETH_TYPE_H_P]!=ETHTYPE_IP_H_V || 
           buf[ETH_TYPE_L_P]!=ETHTYPE_IP_L_V){
                return(0);
        }
        if (buf[IP_HEADER_LEN_VER_P]!=0x45){
                // must be IP V4 and 20 byte header
                return(0);
        }
        while(i<4){
                if(buf[IP_DST_P+i]!=ipaddr[i]){
                        return(0);
                }
                i++;
        }
        return(1);
}

// make a return eth header from a received eth packet
void make_eth(uint8_t *buf)
{
        uint8_t i=0;
        //
        //copy the destination mac from the source and fill my mac into src
        while(i<6){
                buf[ETH_DST_MAC +i]=buf[ETH_SRC_MAC +i];
                buf[ETH_SRC_MAC +i]=macaddr[i];
                i++;
        }
}
void fill_ip_hdr_checksum(uint8_t *buf)
{
        uint16_t ck;
        // clear the 2 byte checksum
        buf[IP_CHECKSUM_P]=0;
        buf[IP_CHECKSUM_P+1]=0;
        buf[IP_FLAGS_P]=0x40; // don't fragment
        buf[IP_FLAGS_P+1]=0;  // fragement offset
        buf[IP_TTL_P]=64; // ttl
        // calculate the checksum:
        ck=checksum(&buf[IP_P], IP_HEADER_LEN,0);
        buf[IP_CHECKSUM_P]=ck>>8;
        buf[IP_CHECKSUM_P+1]=ck& 0xff;
}

// make a return ip header from a received ip packet
void make_ip(uint8_t *buf)
{
        uint8_t i=0;
        while(i<4){
                buf[IP_DST_P+i]=buf[IP_SRC_P+i];
                buf[IP_SRC_P+i]=ipaddr[i];
                i++;
        }
        fill_ip_hdr_checksum(buf);
}

// swap seq and ack number and count ack number up
void step_seq(uint8_t *buf,uint16_t rel_ack_num,uint8_t cp_seq)
{
        uint8_t i;
        uint8_t tseq;
        i=4;
        // sequence numbers:
        // add the rel ack num to SEQACK
        while(i>0){
                rel_ack_num=buf[TCP_SEQ_H_P+i-1]+rel_ack_num;
                tseq=buf[TCP_SEQACK_H_P+i-1];
                buf[TCP_SEQACK_H_P+i-1]=0xff&rel_ack_num;
                if (cp_seq){
                        // copy the acknum sent to us into the sequence number
                        buf[TCP_SEQ_H_P+i-1]=tseq;
                }else{
                        buf[TCP_SEQ_H_P+i-1]= 0; // some preset value
                }
                rel_ack_num=rel_ack_num>>8;
                i--;
        }
}
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

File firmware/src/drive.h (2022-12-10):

/*
 * IncFile1.h
 *
 * Created: 22.04.2016 16:12:38
 *  Author: Nikolay
 */ 
// User defined limits
#define MAX_WIDTH 500//ms
#define MAX_DELAY 7000//ms
#define MAX_CURRENT 900//mA

//Relay driver
#define DRV_PORT PORTC
#define SDI 0
#define SC 2
#define LC 1

//Current control
#define PWM OCR2B
//Current mA to 8bit PWM value fixed point conversion
#define PWM_EXP 11
//PWM_CONST = 2^PWM_EXP*256.0*RSENS/(VCC*1000)
////RSENS - current sens resistor, Ohm
//PWM = I*PWM_CONST/2^PWM_EXP
//I in mA
#define PWM_CONST 419
//Maximal possible current in mA
//#define I_MAX (uint16_t) (65536/PWM_CONST)
//100ms
#define LOW_VCC_TIMEOUT 800
#define CHAN_MASK() UINT16_MAX >> (16 - NPOS)

typedef struct{
uint16_t width;
uint16_t delay;
uint16_t current;
//Natural units
uint16_t phys_width; //ms
uint16_t phys_delay; //ms
uint16_t phys_current; //mA
	
} pulse_str;

extern pulse_str pulse;
//Relay state
extern uint16_t sw_state;
extern uint16_t new_sw_state;
extern uint16_t enabled_pos;

void drive_init();
extern void set_current();

void load_data();
void save_data();

uint8_t do_pulse(uint8_t, uint8_t, uint8_t);

extern uint8_t switch_relays(uint8_t);
extern uint8_t sw_delay(uint16_t, uint8_t);

extern void modify_sw_state(uint16_t*, uint8_t, uint8_t, uint8_t, uint8_t);
extern void chan_off(uint16_t*, uint8_t);

extern void wait_for_vcc();
